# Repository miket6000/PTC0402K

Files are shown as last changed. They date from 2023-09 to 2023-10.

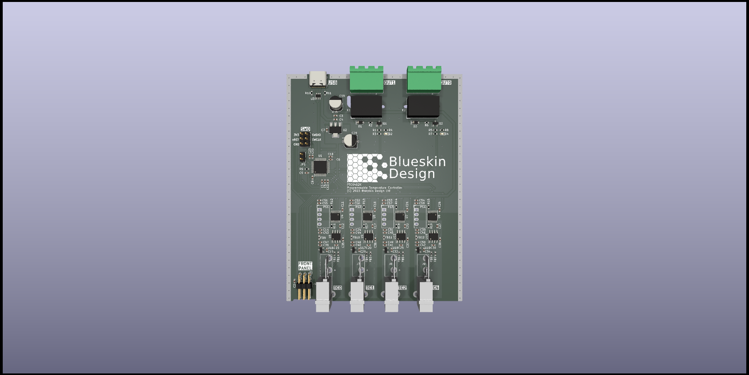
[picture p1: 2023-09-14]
documentation/3d_top_TemperatureLogger.png

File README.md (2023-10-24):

# PTC0402K
A fully isolated (channel to channel and channel to input) four channel, two output programmable temperature controller and logger.

3d_top_TemperatureLogger

This project was built with a few target features in mind:
- Four input channels with at least 0.5C accuracy.
- SCPI interface to interface cleanly with the rest of my lab setup.
- Complete isolation of each channel (at least 230VAC) both between channels and between mains. This allows you to put a thermocouple directly on a live heatsink without risk of damaging the device or anything attached to the other thermocouples.
- A couple of relay outputs for potentially controlling heaters or coolers to allow temperature control.
- USB Type-C for both power and communications for simple setup.

A lot of inspiration came from the very nice project by Jana Marie at https://github.com/Jana-Marie/temperature-logger 

## Status
### Hardware
Rev 1 hardware has arrived. There is a fault in the current schematic where the digital isolators all drive the DO lines, even when their CS line is high. This kills the entire SPI bus. In my Rev 1 hardware I have corrected this by adding a small N-Channel MOSFET between the isolator's output enable pin and ground which is switched by the CS line. This means that normally the output is disabled on all isolators, but is enabled when the CS line is pulled low.

A bigger issue appears to be the temperature error in measureing the cold side junction. Because of the proximity of the MAX31855 to the isolated DCDC converter (which gets warm) and the distance to the thermocouple connector, there can be an error in the reported cold side junction temperature. As thermocouples are differnetial temperature devices, this directly adds to the temperature of the measurement. It looks like this is somewhere in the vicinty of 2-3 degrees C, however this depends on the ambient temperature and how long the entire device is powered which makes it difficult to calibrate out. 

Rev 2 will include the CS line fix and also add external flash to allow on board logging. I'm debating the merits of including a 32kHz crystal for the built in RTC (but then, do I also want a backup battery...) and might end up upgrading the STM32F072 to an STM32F078 for the additional ROM. For the cold junction offset issue I'm still debating options. I could simply move the MAX31855 closer to the junction and further from the DCDC converter, or I could add an additional temperature sensor to the junction itself and provide proper automatic calibration in SW. If I go that path however I end up with a highly integrated solution where I'm effectively not relying on any of the integration and I'd probably be better off with a 16-24bit DAC and discrete voltage reference and an analogue muxer, however this would take up more board space and likely end up costing more.

### Software
A basic test firmware has been written which reads the hot and cold junction temperatures, as well as the thermocouple status and allows them to be read via SCPI. It also allows control of the output relays though no temperature controller or alarms have been written.

The math for computing the corrected NIST polynomial based temperatures is all calculated using fixed point math as there is no FPU in the STM32F072. Rather than computing the polynomials directly on the uC this was done offline to create a lookup table. This is both faster than using floats and more accurate than using fixed point the whole way through as we can use true double precision during intermediate steps of the calculations and only drop to the 16.16 fixed precision format for the final lookup.

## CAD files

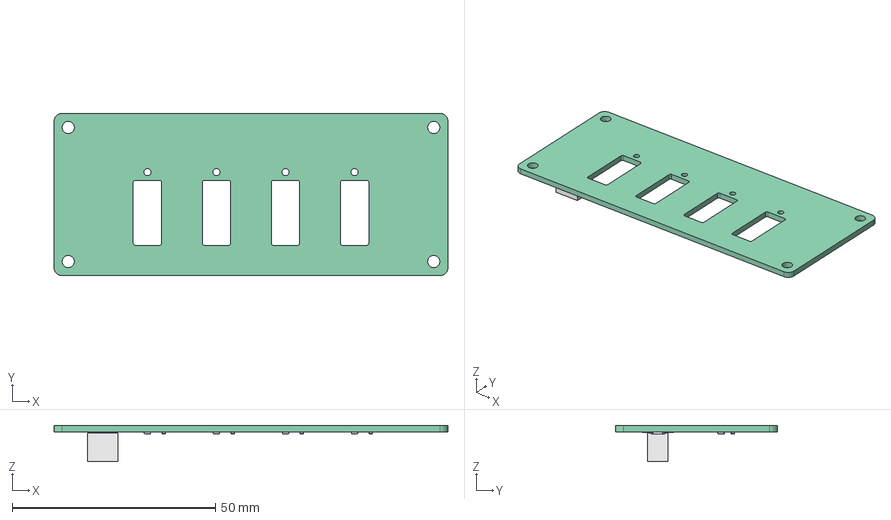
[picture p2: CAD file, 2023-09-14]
mechanical/Front.FCStd
97.0 x 40.0 x 8.90 mm
Pcb_1907
R5_R_0603_1608Metric_a8023c08d09b x 8
J1_PinSocket_2x03_P254mm_Vertical_SMD_16156b7471c3

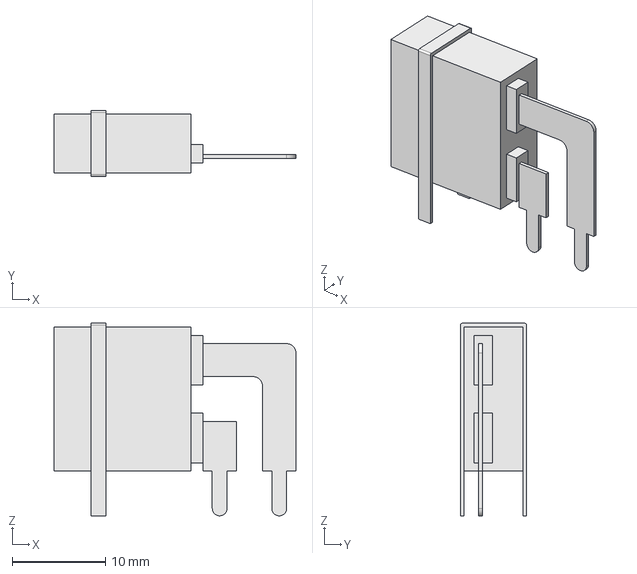
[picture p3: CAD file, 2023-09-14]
mechanical/PCC-SMP-V.FCStd
26.0 x 7.10 x 20.7 mm

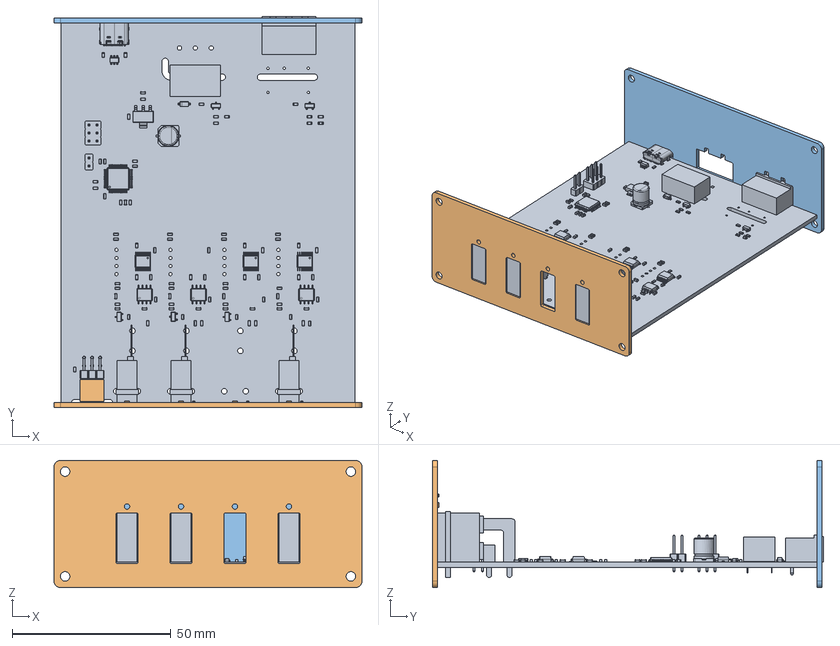
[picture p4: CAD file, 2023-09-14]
mechanical/Assemby.FCStd
97.0 x 123.3 x 40.0 mm
PCB_001
Front_001
Rear_001

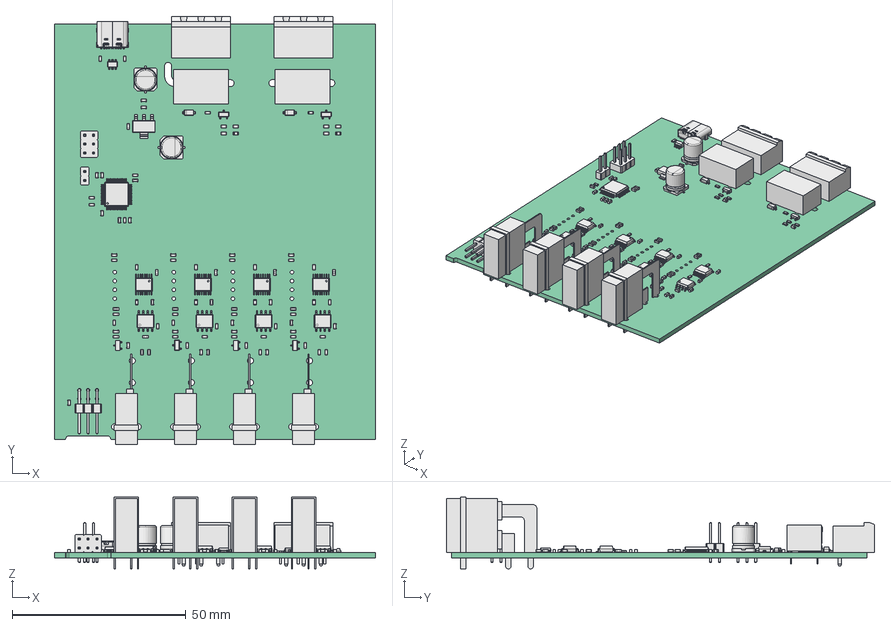
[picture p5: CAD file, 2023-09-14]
mechanical/PCB.FCStd
92.5 x 123.2 x 20.7 mm
Pcb_6b70
U19_SOT_23_b36488b32593 x 6
C33_C_0603_1608Metric_063d88e91227 x 57
J4_PinHeader_2x03_P254mm_Horizontal_694631943000
USB_C_Receptacle_16P_TopMnt_Horizontal_GCT_USB4105-xx-A
USB_C_Receptacle_16P_TopMnt_Horizontal_GCT_USB4105-xx-A001
USB_C_Receptacle_16P_TopMnt_Horizontal_GCT_USB4105-xx-A002
USB_C_Receptacle_16P_TopMnt_Horizontal_GCT_USB4105-xx-A003
USB_C_Receptacle_16P_TopMnt_Horizontal_GCT_USB4105-xx-A004
USB_C_Receptacle_16P_TopMnt_Horizontal_GCT_USB4105-xx-A005
USB_C_Receptacle_16P_TopMnt_Horizontal_GCT_USB4105-xx-A006
USB_C_Receptacle_16P_TopMnt_Horizontal_GCT_USB4105-xx-A007
USB_C_Receptacle_16P_TopMnt_Horizontal_GCT_USB4105-xx-A008
USB_C_Receptacle_16P_TopMnt_Horizontal_GCT_USB4105-xx-A009
USB_C_Receptacle_16P_TopMnt_Horizontal_GCT_USB4105-xx-A010
USB_C_Receptacle_16P_TopMnt_Horizontal_GCT_USB4105-xx-A011
USB_C_Receptacle_16P_TopMnt_Horizontal_GCT_USB4105-xx-A012
USB_C_Receptacle_16P_TopMnt_Horizontal_GCT_USB4105-xx-A013
USB_C_Receptacle_16P_TopMnt_Horizontal_GCT_USB4105-xx-A014
USB_C_Receptacle_16P_TopMnt_Horizontal_GCT_USB4105-xx-A015
USB_C_Receptacle_16P_TopMnt_Horizontal_GCT_USB4105-xx-A016
USB_C_Receptacle_16P_TopMnt_Horizontal_GCT_USB4105-xx-A017
USB_C_Receptacle_16P_TopMnt_Horizontal_GCT_USB4105-xx-A018
USB_C_Receptacle_16P_TopMnt_Horizontal_GCT_USB4105-xx-A019
USB_C_Receptacle_16P_TopMnt_Horizontal_GCT_USB4105-xx-A020
USB_C_Receptacle_16P_TopMnt_Horizontal_GCT_USB4105-xx-A021
USB_C_Receptacle_16P_TopMnt_Horizontal_GCT_USB4105-xx-A022
USB_C_Receptacle_16P_TopMnt_Horizontal_GCT_USB4105-xx-A023
USB_C_Receptacle_16P_TopMnt_Horizontal_GCT_USB4105-xx-A024
USB_C_Receptacle_16P_TopMnt_Horizontal_GCT_USB4105-xx-A025
USB_C_Receptacle_16P_TopMnt_Horizontal_GCT_USB4105-xx-A026
USB_C_Receptacle_16P_TopMnt_Horizontal_GCT_USB4105-xx-A027
USB_C_Receptacle_16P_TopMnt_Horizontal_GCT_USB4105-xx-A028
USB_C_Receptacle_16P_TopMnt_Horizontal_GCT_USB4105-xx-A029
USB_C_Receptacle_16P_TopMnt_Horizontal_GCT_USB4105-xx-A030
USB_C_Receptacle_16P_TopMnt_Horizontal_GCT_USB4105-xx-A031
USB_C_Receptacle_16P_TopMnt_Horizontal_GCT_USB4105-xx-A032
USB_C_Receptacle_16P_TopMnt_Horizontal_GCT_USB4105-xx-A033
USB_C_Receptacle_16P_TopMnt_Horizontal_GCT_USB4105-xx-A034
USB_C_Receptacle_16P_TopMnt_Horizontal_GCT_USB4105-xx-A035
FB2_L_0603_1608Metric_c892ebd92c1a x 12
K2_Relay_SPDT_Omron_G6E_e7cbb446817c x 2
R13_R_0603_1608Metric_337461c32d41 x 19
J8_Body_0be8fa092d88 x 4
J5_PinHeader_2x03_P254mm_Vertical_61c661ac012c
U5_SSOP_16_39x49mm_P0635mm_b9b537abdd21 x 4
U1_LQFP_48_7x7mm_P05mm_b04207c67cd0
D3_D_SOD_123_1aa070bb9a73 x 2
U12_SOIC_8_39x49mm_P127mm_51daad1ce575 x 4
D2_LED_0603_1608Metric_81a1771d8797 x 2
C59_CP_Elec_63x77_526fc9ffda22 x 2
U3_SOT_23_6_5fe2d78700b6
U2_SOT_223_7fa0f1d7f736
J1_MSTBA_01x03_G_5_00mm_6adaa229897f x 2
JP1_PinHeader_1x02_P254mm_Vertical_b7242ec4fe1f

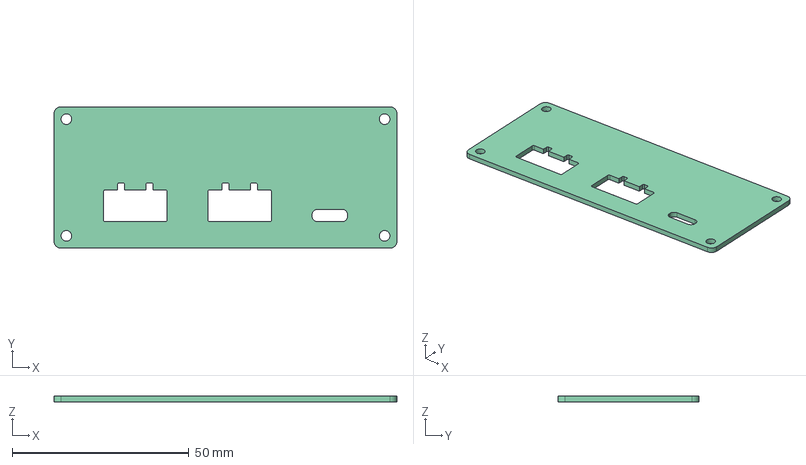
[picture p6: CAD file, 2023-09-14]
mechanical/Rear.FCStd
97.0 x 40.0 x 1.60 mm

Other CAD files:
mechanical/PCC-SMP-V-Body.step

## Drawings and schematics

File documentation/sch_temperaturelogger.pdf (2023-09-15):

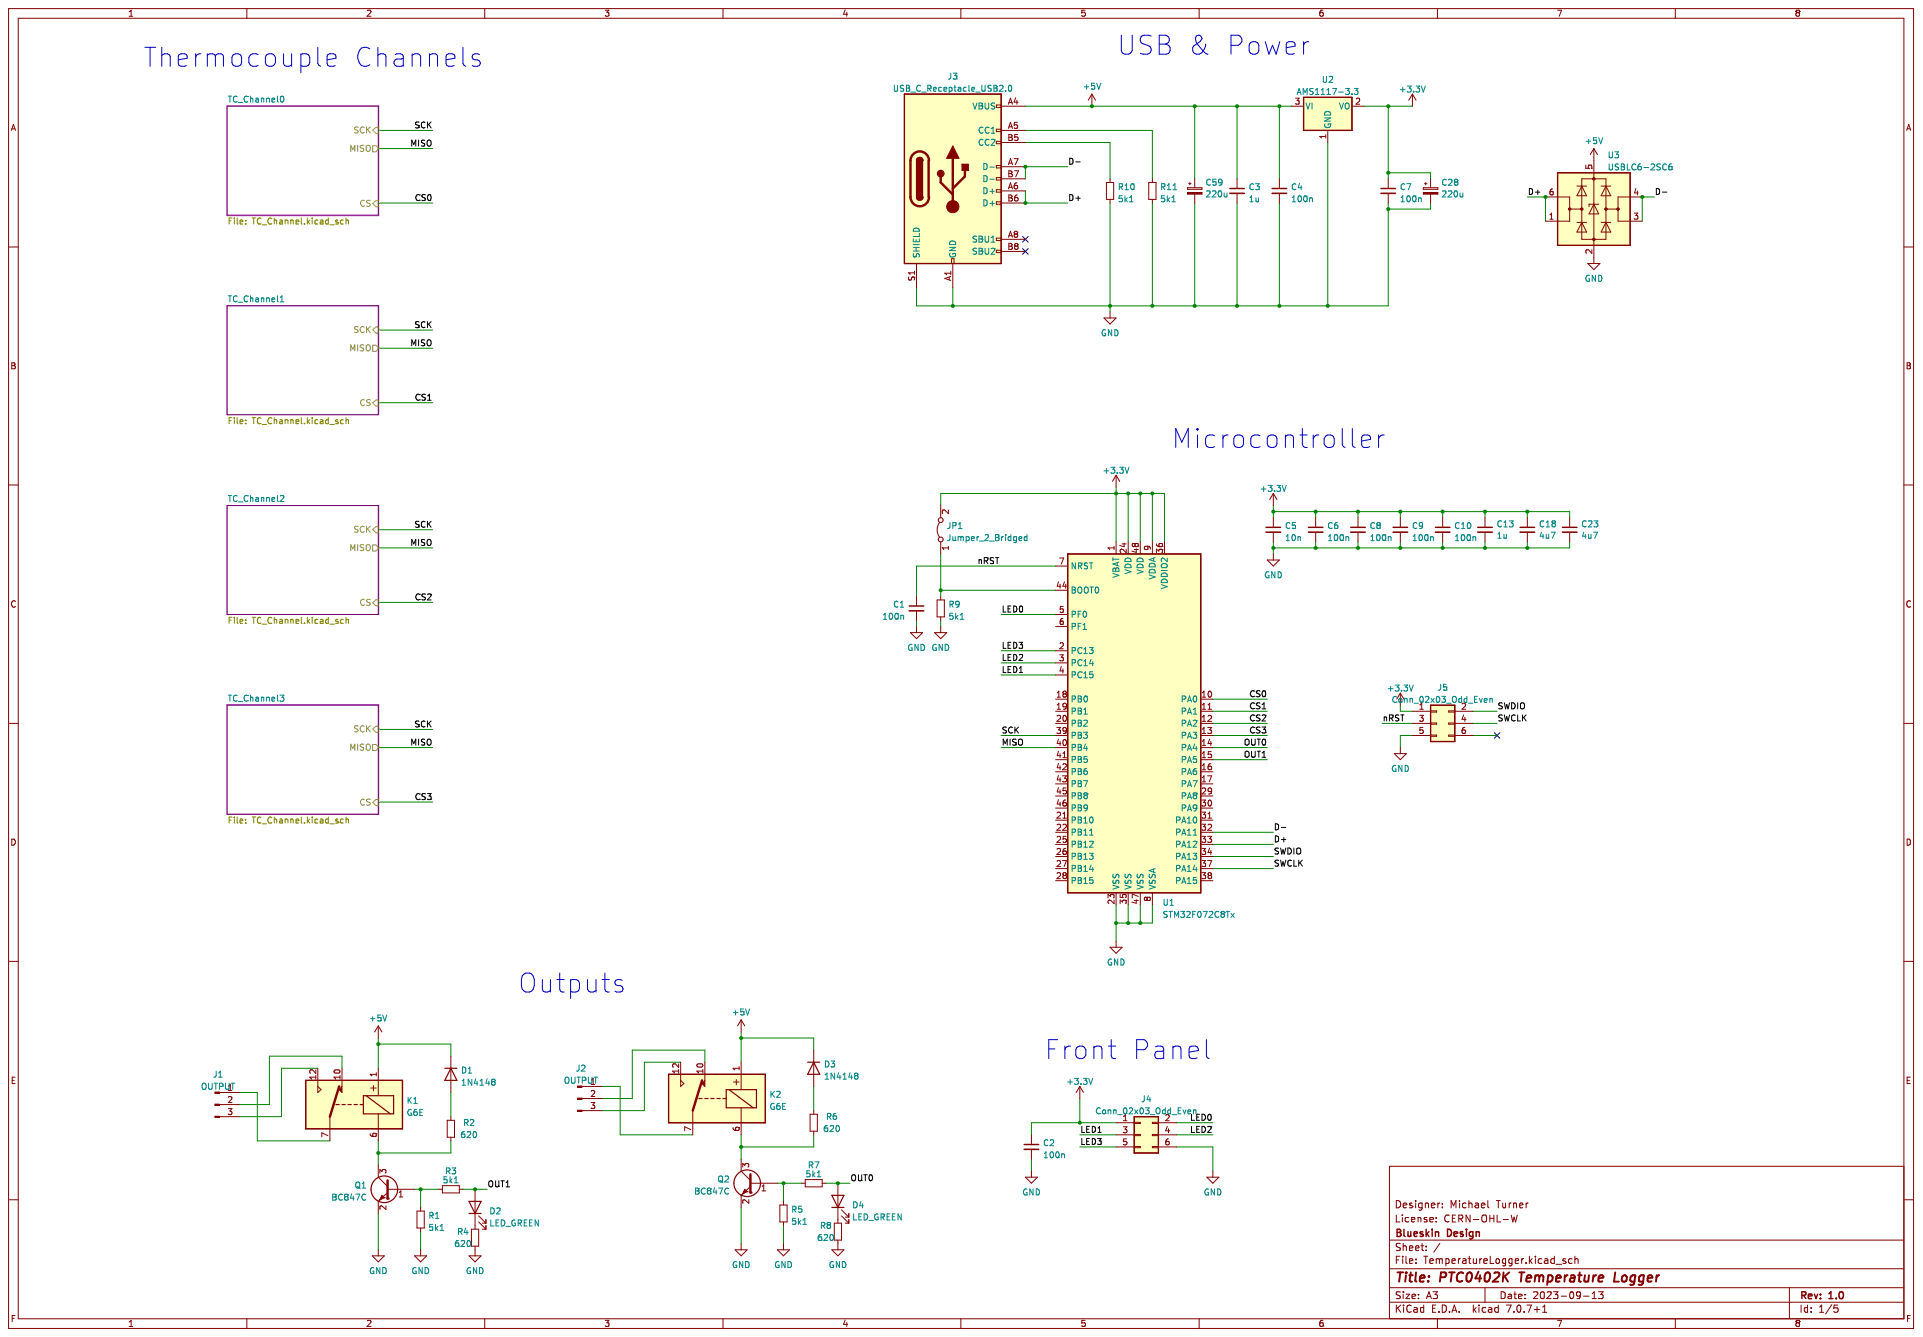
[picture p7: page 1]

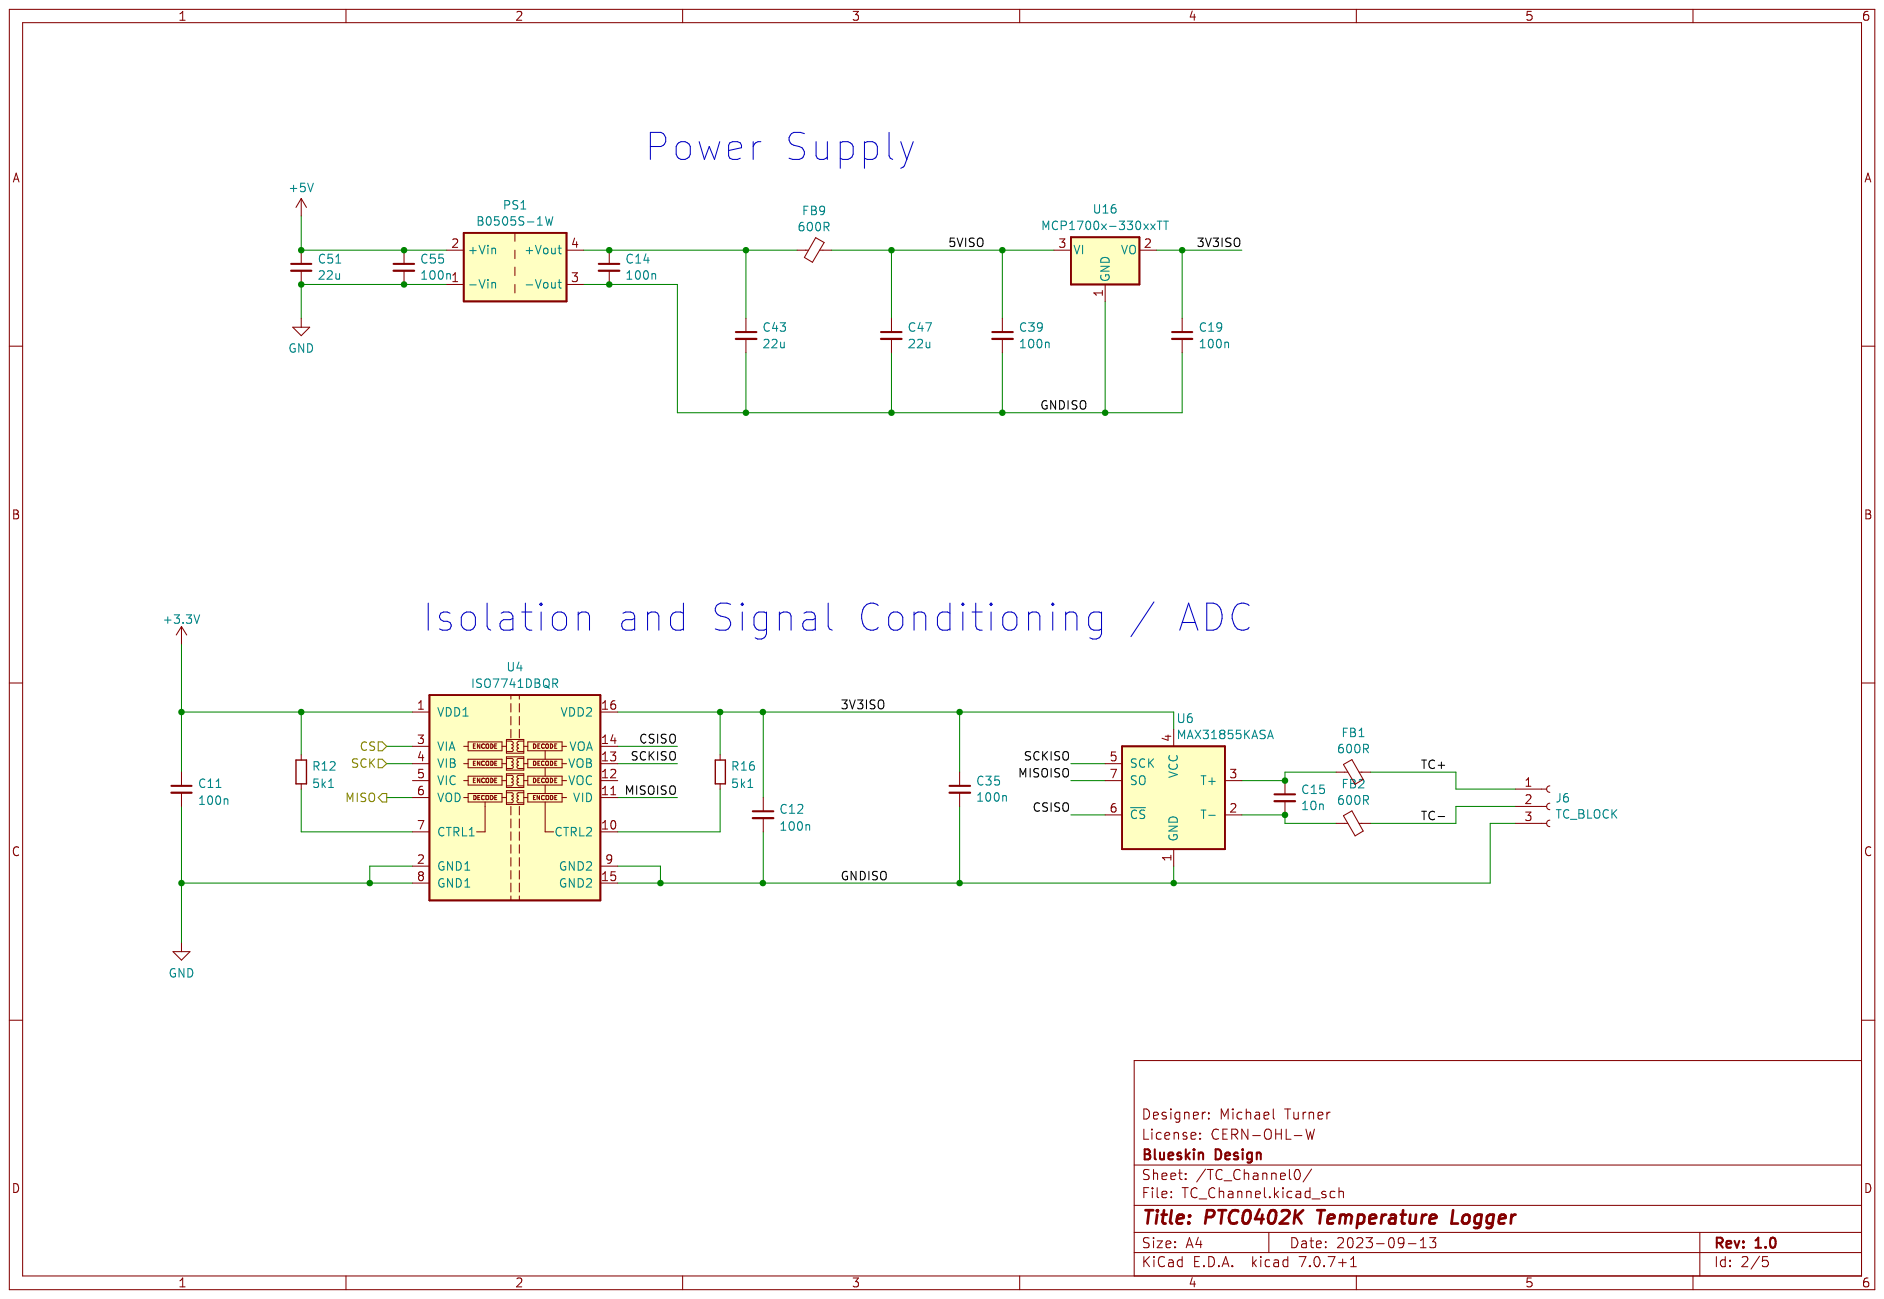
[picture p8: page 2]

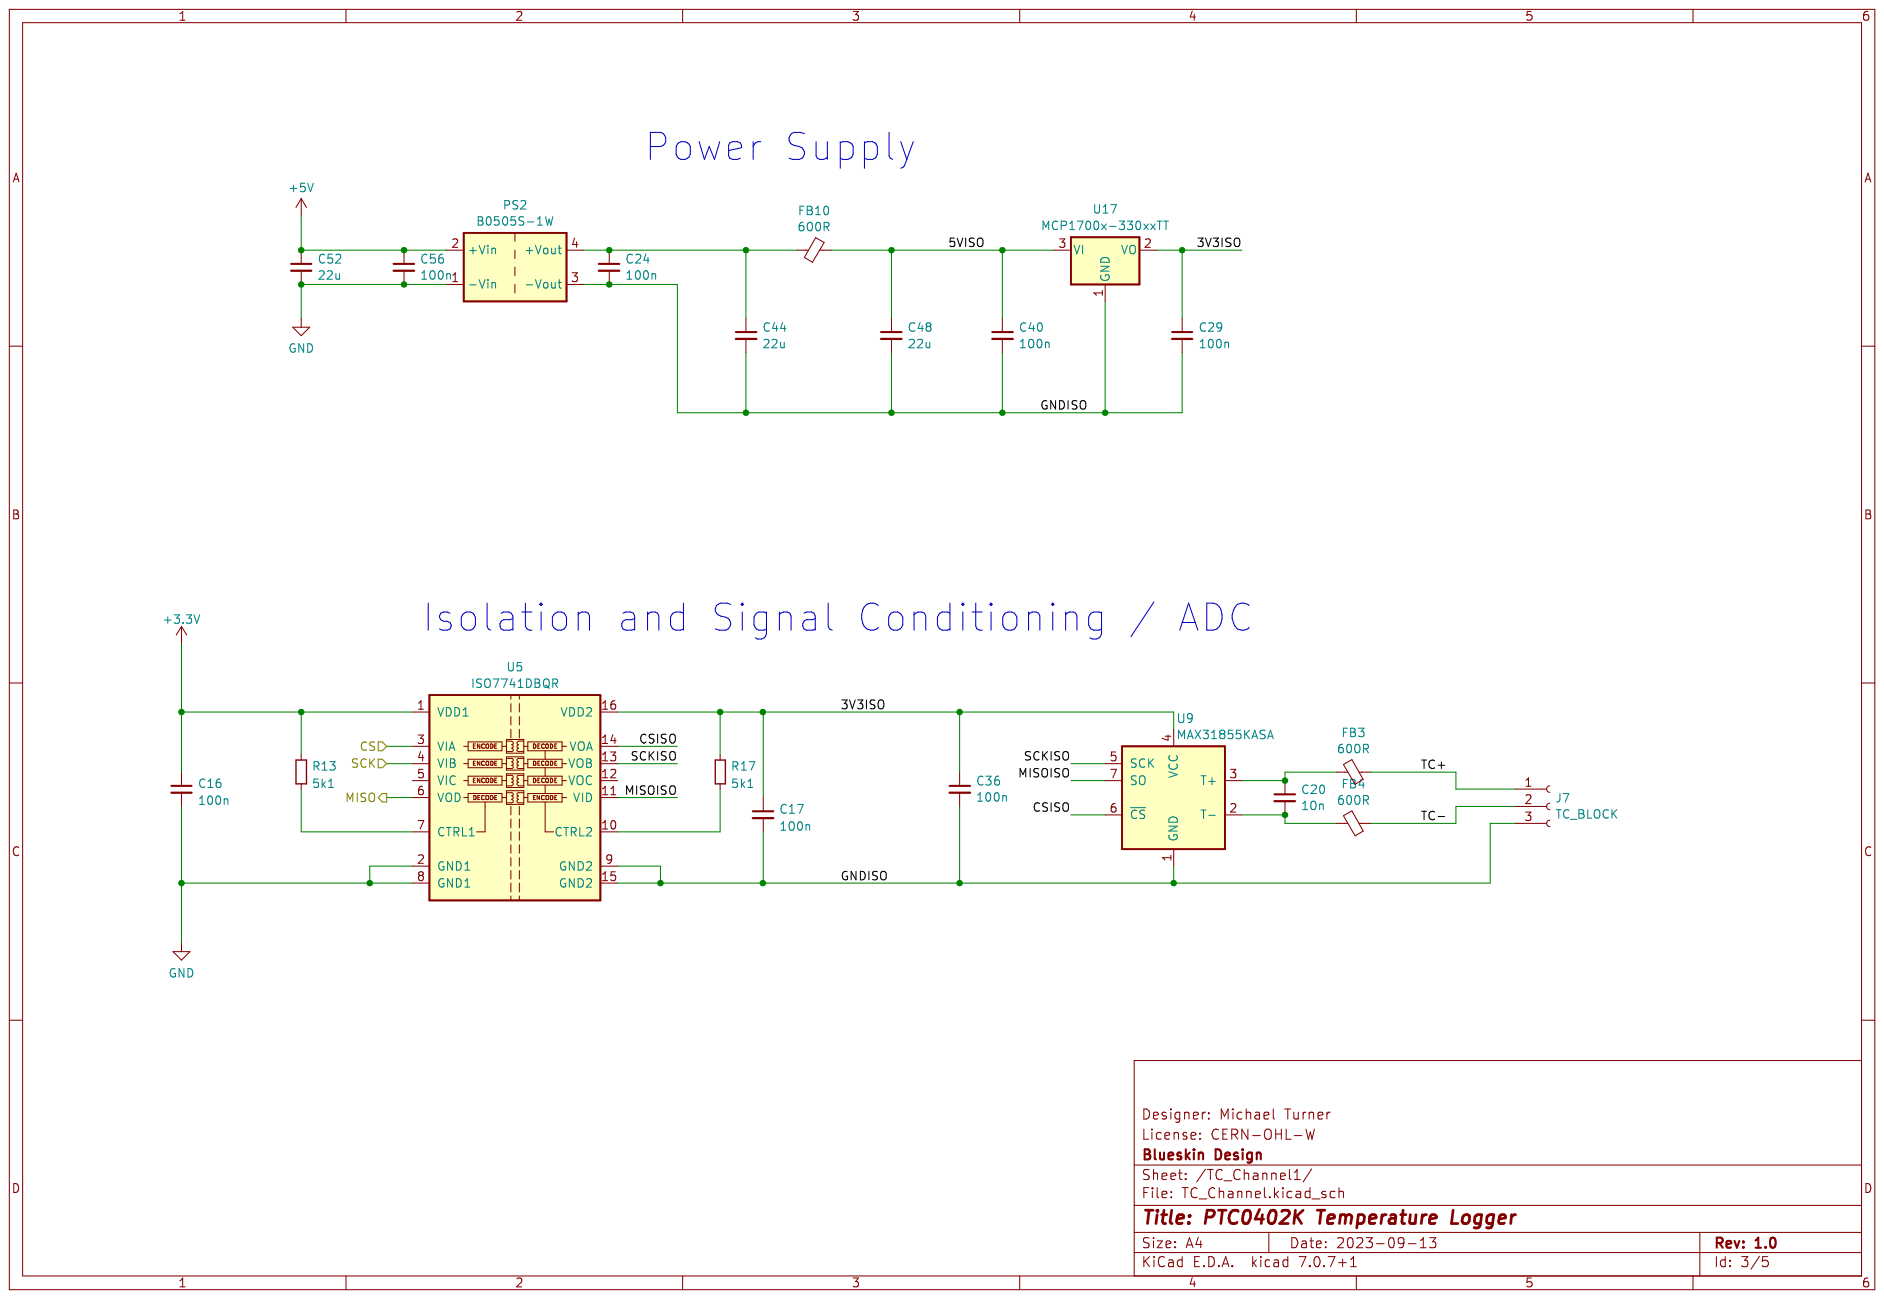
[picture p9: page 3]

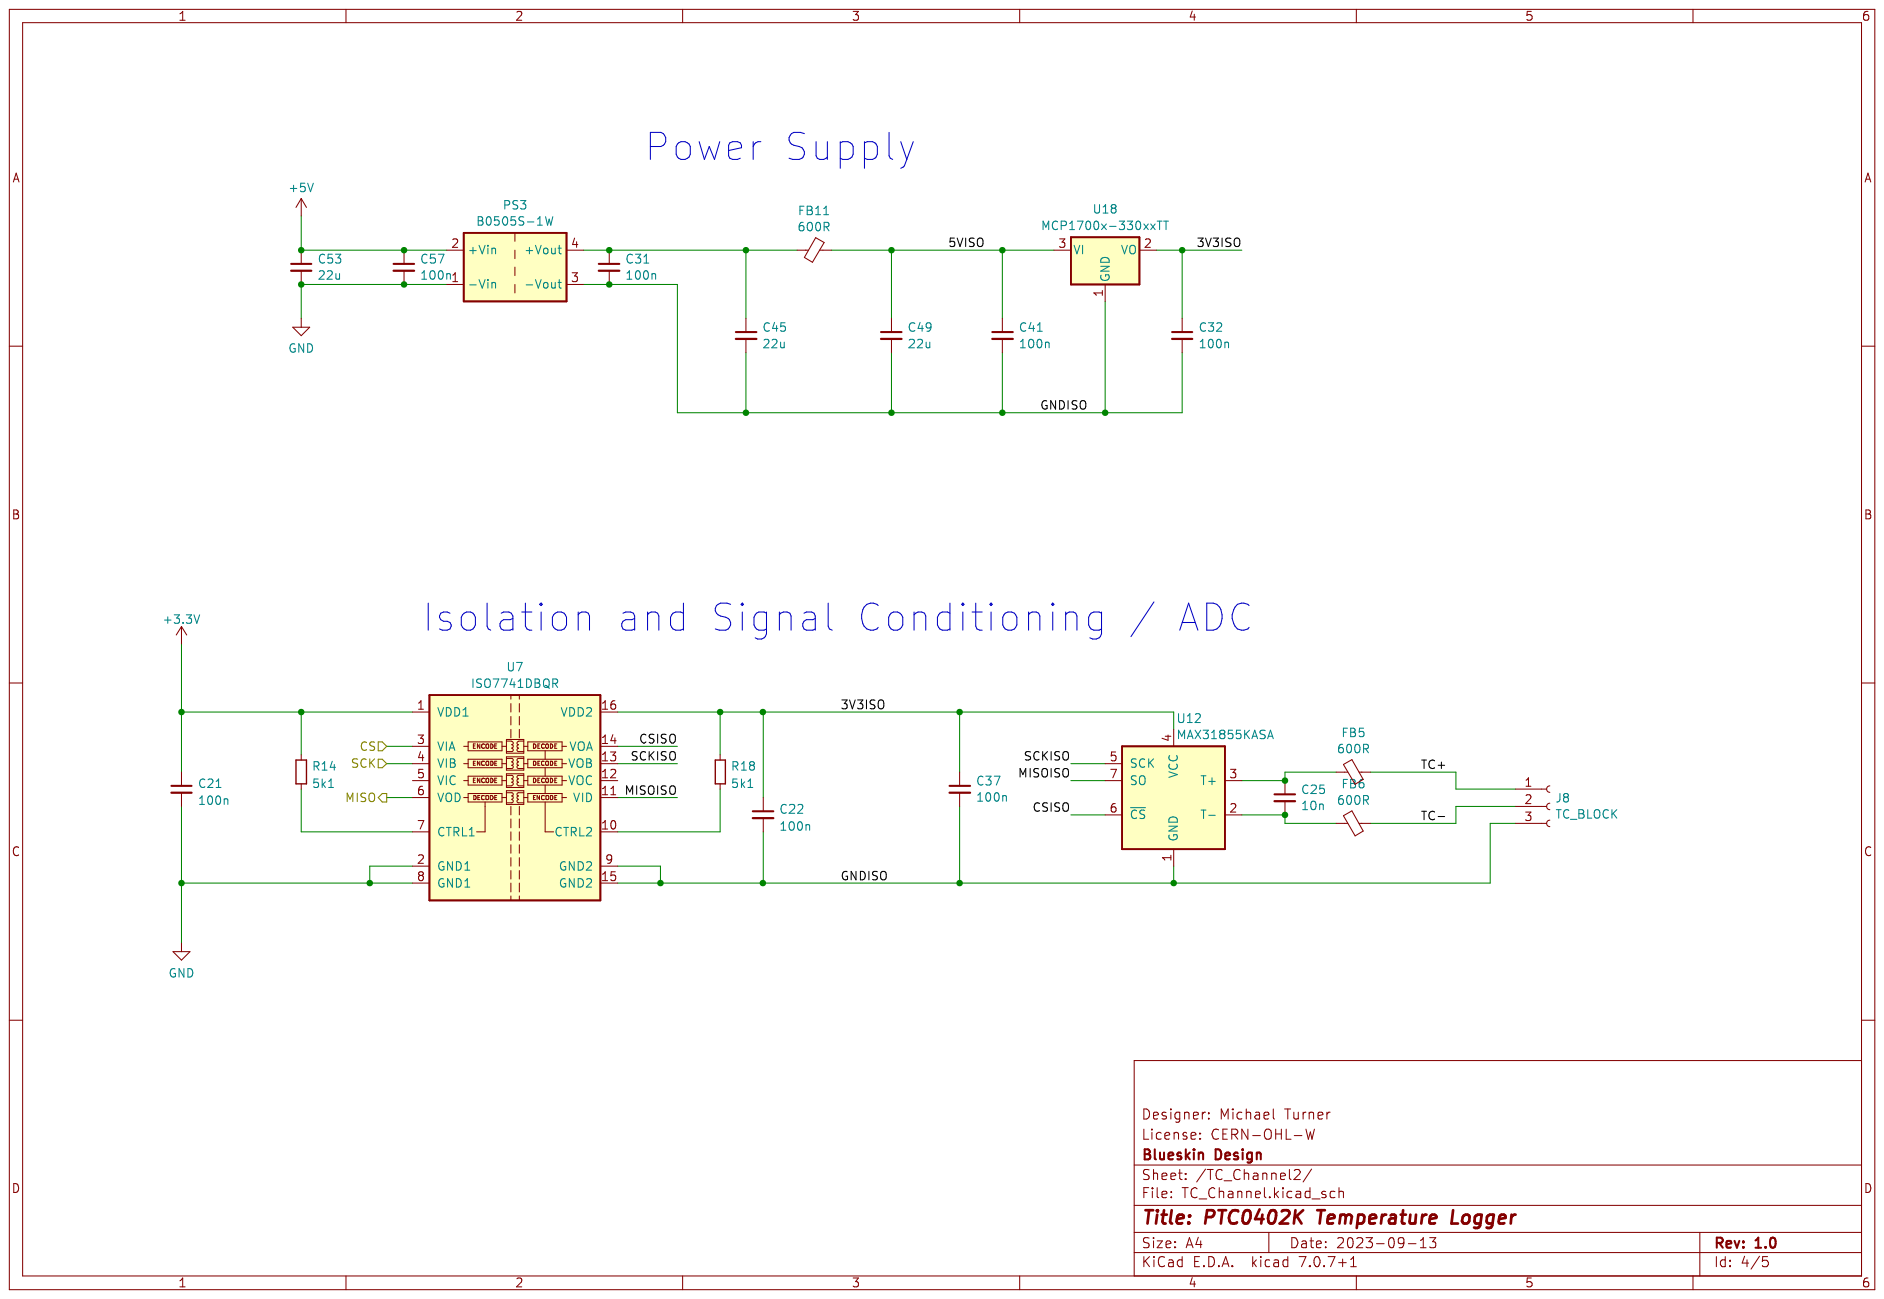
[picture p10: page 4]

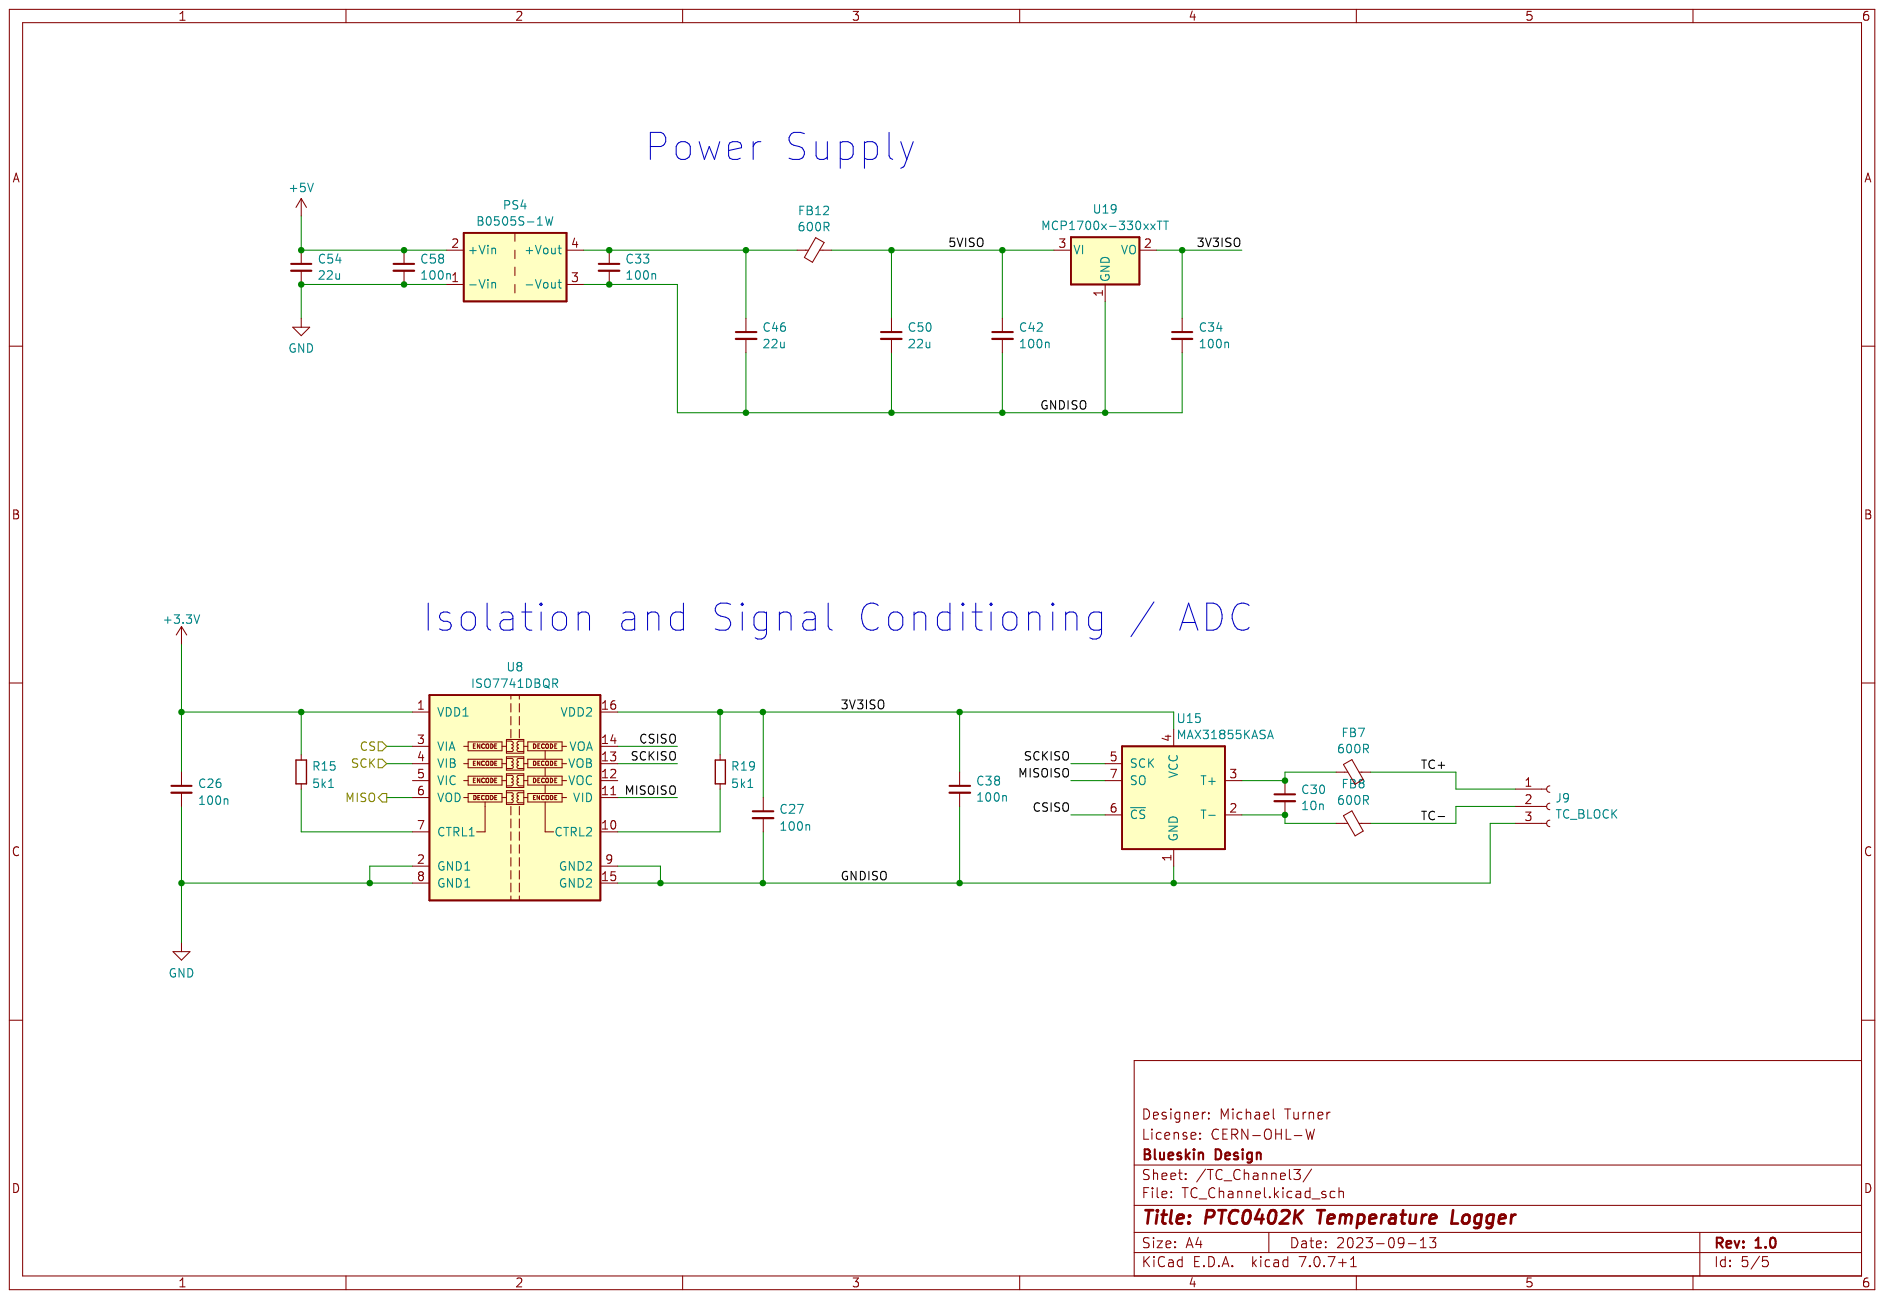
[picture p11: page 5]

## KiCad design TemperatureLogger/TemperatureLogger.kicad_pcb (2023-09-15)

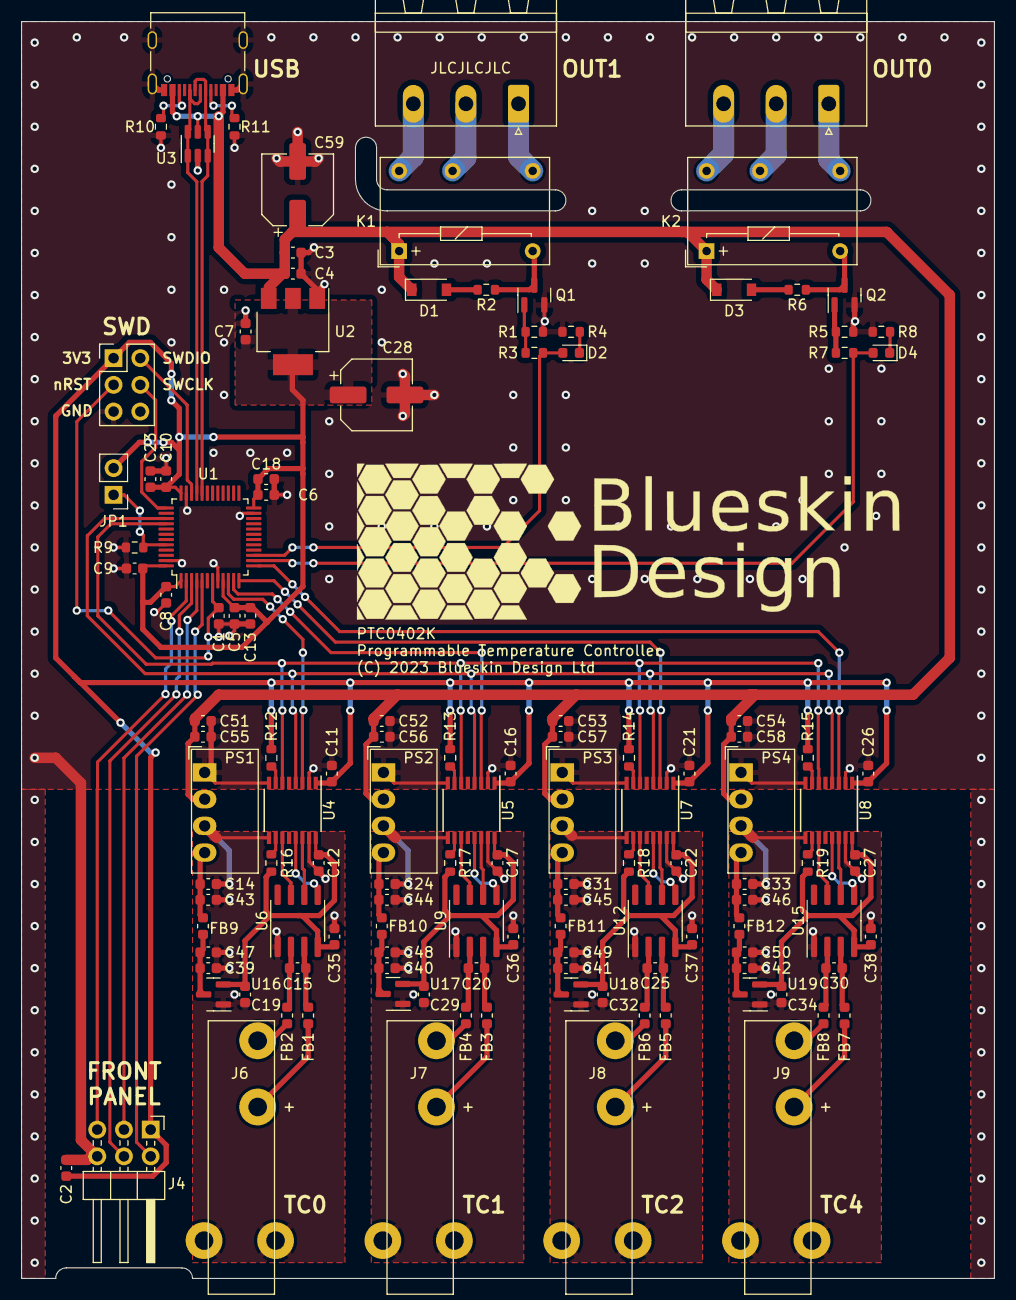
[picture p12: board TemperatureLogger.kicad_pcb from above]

Board: 2 copper layers, 92.5 x 119.5 mm, 127 parts (0 on the bottom side), 89 nets.

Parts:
C1, C2, C4, C6, C7, C8, C9, C10, C11, C12, C14, C16, C17, C19, C21, C22, C24, C26, C27, C29, C31, C32, C33, C34, C35, C36, C37, C38, C39, C40, C41, C42, C55, C56, C57, C58: 100n; C_0603_1608Metric
C3, C13: 1u; C_0603_1608Metric
C5, C15, C20, C25, C30: 10n; C_0603_1608Metric
C18, C23: 4u7; C_0603_1608Metric
C28, C59: 220u; CP_Elec_6.3x7.7
C43, C44, C45, C46, C47, C48, C49, C50, C51, C52, C53, C54: 22u; C_0603_1608Metric
D1, D3: 1N4148; D_SOD-123
D2, D4: LED_GREEN; LED_0603_1608Metric
FB1, FB2, FB3, FB4, FB5, FB6, FB7, FB8, FB9, FB10, FB11, FB12: 600R; L_0603_1608Metric
J1, J2: OUTPUT; PhoenixContact_MSTBA_2,5_3-G_1x03_P5.00mm_Horizontal
J3: USB_C_Receptacle_USB2.0; USB_C_Receptacle_Palconn_UTC16-G
J4: Conn_02x03_Odd_Even; PinHeader_2x03_P2.54mm_Horizontal
J5: Conn_02x03_Odd_Even; PinHeader_2x03_P2.54mm_Vertical
J6, J7, J8, J9: TC_BLOCK; PCC-SMP-V
JP1: Jumper_2_Bridged; PinHeader_1x02_P2.54mm_Vertical
K1, K2: G6E; Relay_SPDT_Omron_G6E
PS1, PS2, PS3, PS4: B0505S-1W; Converter_DCDC_Murata_MEE1SxxxxSC_THT
Q1, Q2: BC847C; SOT-23
R1, R3, R5, R7, R9, R10, R11, R12, R13, R14, R15, R16, R17, R18, R19: 5k1; R_0603_1608Metric
R2, R4, R6, R8: 620; R_0603_1608Metric
U1: STM32F072C8Tx; LQFP-48_7x7mm_P0.5mm
U2: AMS1117-3.3; SOT-223-3_TabPin2
U3: USBLC6-2SC6; SOT-23-6
U4, U5, U7, U8: ISO7741DBQR; SSOP-16_3.9x4.9mm_P0.635mm
U6, U9, U12, U15: MAX31855KASA; SOIC-8_3.9x4.9mm_P1.27mm
U16, U17, U18, U19: MCP1700x-330xxTT; SOT-23

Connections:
+3.3V: C2.1, C5.1, C6.1, C7.1, C8.1, C9.1, C10.1, C11.1, C13.1, C16.1, C18.1, C21.1, C23.1, C26.1, C28.1, J4.1, J5.1, JP1.2 (B), R12.2, R13.2, R14.2, R15.2, U1.1 (VBAT), U1.9 (VDDA), U1.24 (VDD), U1.36 (VDDIO2), U1.48 (VDD), U2.2 (VO), U4.1 (VDD1), U5.1 (VDD1), U7.1 (VDD1), U8.1 (VDD1)
+5V: C3.1, C4.1, C51.1, C52.1, C53.1, C54.1, C55.1, C56.1, C57.1, C58.1, C59.1, D1.1 (K), D3.1 (K), J3.A4 (VBUS), J3.A9 (VBUS), J3.B4 (VBUS), J3.B9 (VBUS), K1.1, K2.1, PS1.2 (+Vin), PS2.2 (+Vin), PS3.2 (+Vin), PS4.2 (+Vin), U2.3 (VI), U3.5 (VBUS)
/CS0: U1.10 (PA0), U4.3 (VIA)
/CS1: U1.11 (PA1), U5.3 (VIA)
/CS2: U1.12 (PA2), U7.3 (VIA)
/CS3: U1.13 (PA3), U8.3 (VIA)
/D+: J3.A6 (D+), J3.B6 (D+), U1.33 (PA12), U3.1 (I/O1), U3.6 (I/O1)
/D-: J3.A7 (D-), J3.B7 (D-), U1.32 (PA11), U3.3 (I/O2), U3.4 (I/O2)
/LED0: J4.2, U1.5 (PF0)
/LED1: J4.3, U1.4 (PC15)
/LED2: J4.4, U1.3 (PC14)
/LED3: J4.5, U1.2 (PC13)
/MISO: U1.40 (PB4), U4.6 (VOD), U5.6 (VOD), U7.6 (VOD), U8.6 (VOD)
/OUT0: D4.2 (A), R7.2, U1.14 (PA4)
/OUT1: D2.2 (A), R3.2, U1.15 (PA5)
/SCK: U1.39 (PB3), U4.4 (VIB), U5.4 (VIB), U7.4 (VIB), U8.4 (VIB)
/SWCLK: J5.4, U1.37 (PA14)
/SWDIO: J5.2, U1.34 (PA13)
/TC_Channel0/3V3ISO: C12.1, C19.1, C35.1, R16.2, U4.16 (VDD2), U6.4 (VCC), U16.2 (VO)
/TC_Channel0/5VISO: C39.1, C47.1, FB9.2, U16.3 (VI)
/TC_Channel0/CSISO: U4.14 (VOA), U6.6 (~CS)
/TC_Channel0/GNDISO: C12.2, C14.2, C19.2, C35.2, C39.2, C43.2, C47.2, J6.3, PS1.3 (-Vout), U4.9 (GND2), U4.15 (GND2), U6.1 (GND), U16.1 (GND)
/TC_Channel0/MISOISO: U4.11 (VID), U6.7 (SO)
/TC_Channel0/SCKISO: U4.13 (VOB), U6.5 (SCK)
/TC_Channel0/TC+: FB1.1, J6.1
/TC_Channel0/TC-: FB2.1, J6.2
/TC_Channel1/3V3ISO: C17.1, C29.1, C36.1, R17.2, U5.16 (VDD2), U9.4 (VCC), U17.2 (VO)
/TC_Channel1/5VISO: C40.1, C48.1, FB10.2, U17.3 (VI)
/TC_Channel1/CSISO: U5.14 (VOA), U9.6 (~CS)
/TC_Channel1/GNDISO: C17.2, C24.2, C29.2, C36.2, C40.2, C44.2, C48.2, J7.3, PS2.3 (-Vout), U5.9 (GND2), U5.15 (GND2), U9.1 (GND), U17.1 (GND)
/TC_Channel1/MISOISO: U5.11 (VID), U9.7 (SO)
/TC_Channel1/SCKISO: U5.13 (VOB), U9.5 (SCK)
/TC_Channel1/TC+: FB3.1, J7.1
/TC_Channel1/TC-: FB4.1, J7.2
/TC_Channel2/3V3ISO: C22.1, C32.1, C37.1, R18.2, U7.16 (VDD2), U12.4 (VCC), U18.2 (VO)
/TC_Channel2/5VISO: C41.1, C49.1, FB11.2, U18.3 (VI)
/TC_Channel2/CSISO: U7.14 (VOA), U12.6 (~CS)
/TC_Channel2/GNDISO: C22.2, C31.2, C32.2, C37.2, C41.2, C45.2, C49.2, J8.3, PS3.3 (-Vout), U7.9 (GND2), U7.15 (GND2), U12.1 (GND), U18.1 (GND)
/TC_Channel2/MISOISO: U7.11 (VID), U12.7 (SO)
/TC_Channel2/SCKISO: U7.13 (VOB), U12.5 (SCK)
/TC_Channel2/TC+: FB5.1, J8.1
/TC_Channel2/TC-: FB6.1, J8.2
/TC_Channel3/3V3ISO: C27.1, C34.1, C38.1, R19.2, U8.16 (VDD2), U15.4 (VCC), U19.2 (VO)
/TC_Channel3/5VISO: C42.1, C50.1, FB12.2, U19.3 (VI)
/TC_Channel3/CSISO: U8.14 (VOA), U15.6 (~CS)
/TC_Channel3/GNDISO: C27.2, C33.2, C34.2, C38.2, C42.2, C46.2, C50.2, J9.3, PS4.3 (-Vout), U8.9 (GND2), U8.15 (GND2), U15.1 (GND), U19.1 (GND)
/TC_Channel3/MISOISO: U8.11 (VID), U15.7 (SO)
/TC_Channel3/SCKISO: U8.13 (VOB), U15.5 (SCK)
/TC_Channel3/TC+: FB7.1, J9.1
/TC_Channel3/TC-: FB8.1, J9.2
/nRST: C1.1, J5.3, U1.7 (NRST)
GND: C1.2, C2.2, C3.2, C4.2, C5.2, C6.2, C7.2, C8.2, C9.2, C10.2, C11.2, C13.2, C16.2, C18.2, C21.2, C23.2, C26.2, C28.2, C51.2, C52.2, C53.2, C54.2, C55.2, C56.2, C57.2, C58.2, C59.2, J3.A1 (GND), J3.A12 (GND), J3.B1 (GND), J3.B12 (GND), J3.S1 (SHIELD), J4.6, J5.5, PS1.1 (-Vin), PS2.1 (-Vin), PS3.1 (-Vin), PS4.1 (-Vin), Q1.2 (E), Q2.2 (E), R1.1, R4.1, R5.1, R8.1, R9.2, R10.2, R11.2, U1.8 (VSSA), U1.23 (VSS), U1.35 (VSS), U1.47 (VSS), U2.1 (GND), U3.2 (GND), U4.2 (GND1), U4.8 (GND1), U5.2 (GND1), U5.8 (GND1), U7.2 (GND1), U7.8 (GND1), U8.2 (GND1), U8.8 (GND1)
unnamed: D1.2 (A), R2.2
unnamed: D2.1 (K), R4.2
unnamed: D3.2 (A), R6.2
unnamed: D4.1 (K), R8.2
unnamed: J1.1, K1.7
unnamed: J1.2, K1.10
unnamed: J1.3, K1.12
unnamed: J2.1, K2.7
unnamed: J2.2, K2.10
unnamed: J2.3, K2.12
unnamed: J3.A5 (CC1), R11.1
unnamed: J3.B5 (CC2), R10.1
unnamed: JP1.1 (A), R9.1, U1.44 (BOOT0)
unnamed: C14.1, C43.1, FB9.1, PS1.4 (+Vout)
unnamed: C24.1, C44.1, FB10.1, PS2.4 (+Vout)
unnamed: C31.1, C45.1, FB11.1, PS3.4 (+Vout)
unnamed: C33.1, C46.1, FB12.1, PS4.4 (+Vout)
unnamed: Q1.1 (B), R1.2, R3.1
unnamed: K1.6, Q1.3 (C), R2.1
unnamed: Q2.1 (B), R5.2, R7.1
unnamed: K2.6, Q2.3 (C), R6.1
unnamed: R12.1, U4.7 (CTRL1)
unnamed: R16.1, U4.10 (CTRL2)
unnamed: R13.1, U5.7 (CTRL1)
unnamed: R17.1, U5.10 (CTRL2)
unnamed: C15.1, FB1.2, U6.3 (T+)
unnamed: C15.2, FB2.2, U6.2 (T-)
unnamed: R14.1, U7.7 (CTRL1)
unnamed: R18.1, U7.10 (CTRL2)
unnamed: R15.1, U8.7 (CTRL1)
unnamed: R19.1, U8.10 (CTRL2)
unnamed: C20.1, FB3.2, U9.3 (T+)
unnamed: C20.2, FB4.2, U9.2 (T-)
unnamed: C25.1, FB5.2, U12.3 (T+)
unnamed: C25.2, FB6.2, U12.2 (T-)
unnamed: C30.1, FB7.2, U15.3 (T+)
unnamed: C30.2, FB8.2, U15.2 (T-)

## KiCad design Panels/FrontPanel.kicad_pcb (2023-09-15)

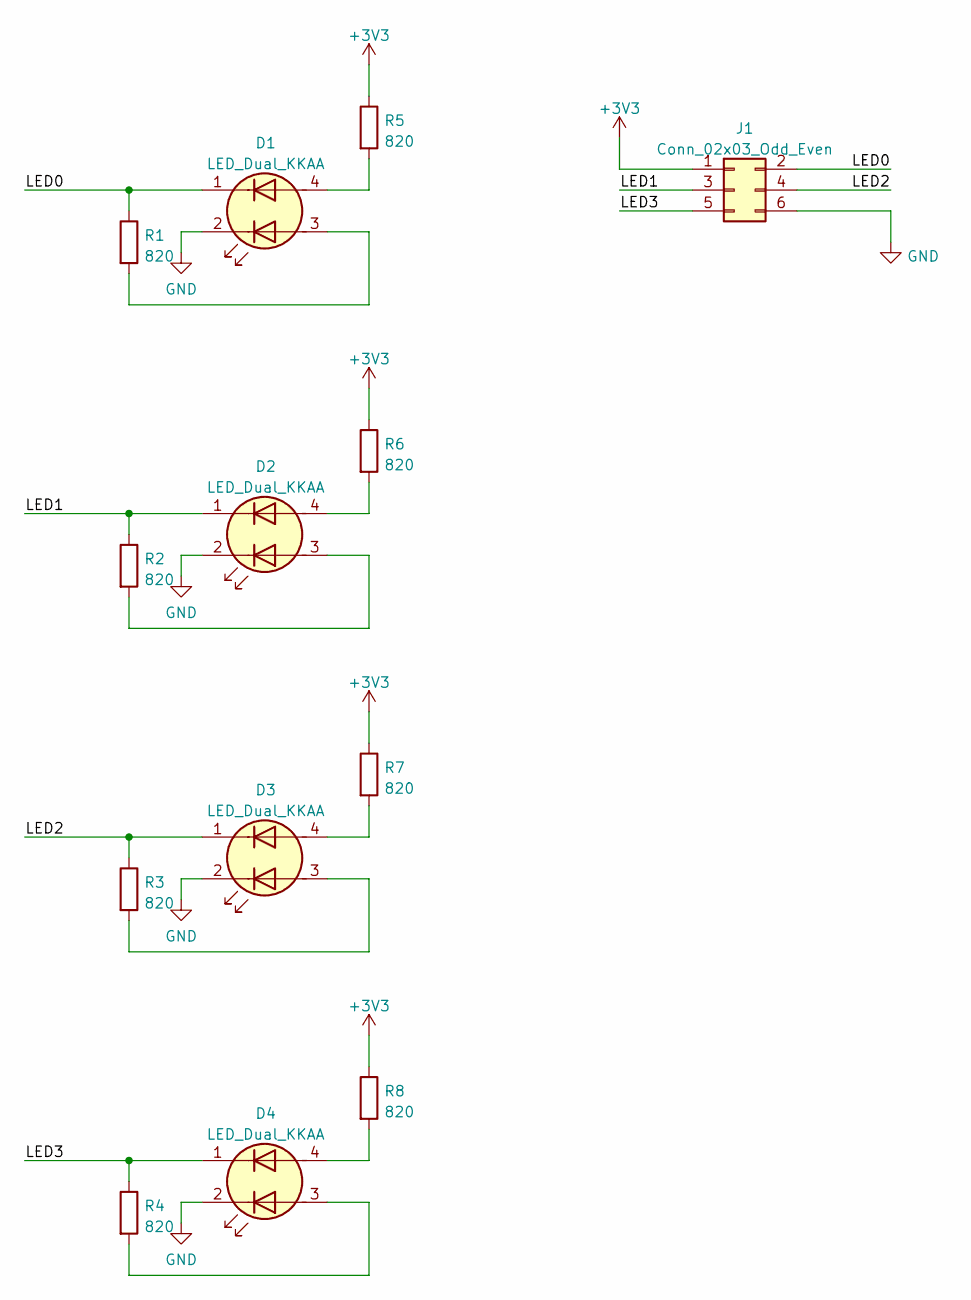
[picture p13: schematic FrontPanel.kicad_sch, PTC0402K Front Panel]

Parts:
D1, D2, D3, D4: LED_Dual_KKAA; Wurth_Bicolor_Reverse_Mount_LED
J1: Conn_02x03_Odd_Even; PinSocket_2x03_P2.54mm_Vertical_SMD
R1, R2, R3, R4, R5, R6, R7, R8: 820; R_0603_1608Metric_Pad0.98x0.95mm_HandSolder

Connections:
+3V3: J1.1, R5.1, R6.1, R7.1, R8.1
/LED0: D1.1 (K2), J1.2, R1.1
/LED1: D2.1 (K2), J1.3, R2.1
/LED2: D3.1 (K2), J1.4, R3.1
/LED3: D4.1 (K2), J1.5, R4.1
GND: D1.2 (K1), D2.2 (K1), D3.2 (K1), D4.2 (K1), J1.6
unnamed: D1.3 (A1), R1.2
unnamed: D1.4 (A2), R5.2
unnamed: D2.3 (A1), R2.2
unnamed: D2.4 (A2), R6.2
unnamed: D3.3 (A1), R3.2
unnamed: D3.4 (A2), R7.2
unnamed: D4.3 (A1), R4.2
unnamed: D4.4 (A2), R8.2

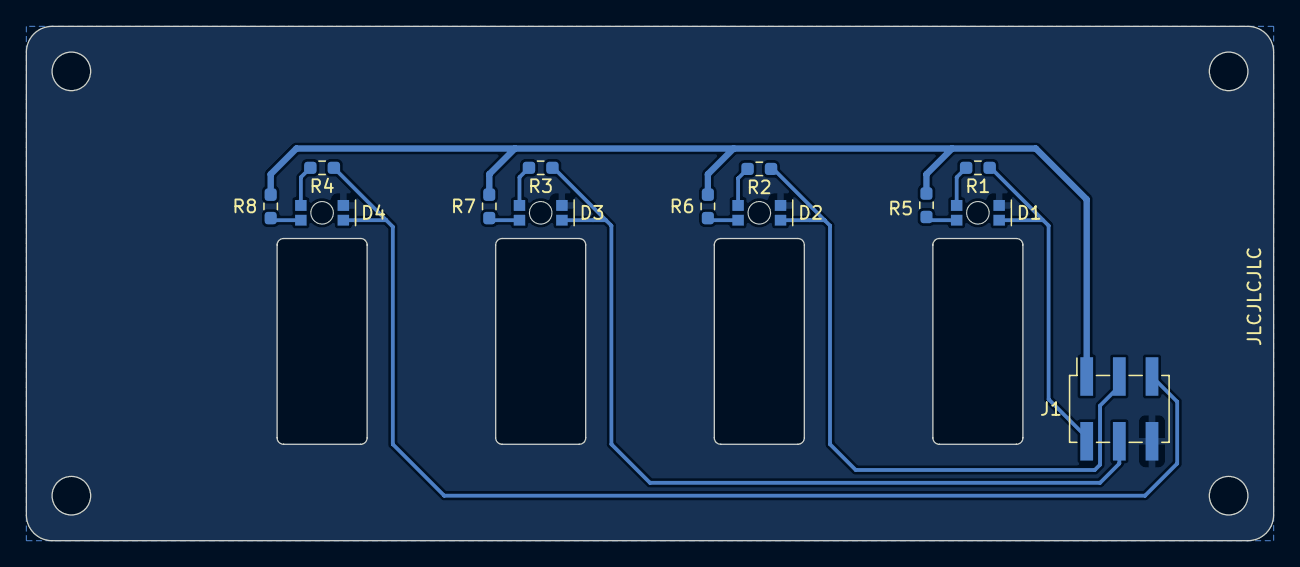
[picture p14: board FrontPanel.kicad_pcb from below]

Board: 2 copper layers, 97.0 x 40.0 mm, 13 parts (13 on the bottom side), 14 nets.

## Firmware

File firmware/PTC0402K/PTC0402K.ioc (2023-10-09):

#MicroXplorer Configuration settings - do not modify
CAD.formats=[{"id"\:42,"cad_product"\:"KiCAD v6+","cad_family"\:"KiCAD"}]
CAD.pinconfig=Dual
CAD.provider=
Dma.Request0=SPI1_RX
Dma.RequestsNb=1
Dma.SPI1_RX.0.Direction=DMA_PERIPH_TO_MEMORY
Dma.SPI1_RX.0.Instance=DMA1_Channel2
Dma.SPI1_RX.0.MemDataAlignment=DMA_MDATAALIGN_BYTE
Dma.SPI1_RX.0.MemInc=DMA_MINC_ENABLE
Dma.SPI1_RX.0.Mode=DMA_NORMAL
Dma.SPI1_RX.0.PeriphDataAlignment=DMA_PDATAALIGN_BYTE
Dma.SPI1_RX.0.PeriphInc=DMA_PINC_DISABLE
Dma.SPI1_RX.0.Priority=DMA_PRIORITY_LOW
Dma.SPI1_RX.0.RequestParameters=Instance,Direction,PeriphInc,MemInc,PeriphDataAlignment,MemDataAlignment,Mode,Priority
File.Version=6
GPIO.groupedBy=Show All
KeepUserPlacement=false
Mcu.CPN=STM32F072C8T6TR
Mcu.Family=STM32F0
Mcu.IP0=DMA
Mcu.IP1=NVIC
Mcu.IP2=RCC
Mcu.IP3=SPI1
Mcu.IP4=SYS
Mcu.IP5=TIM14
Mcu.IP6=USB
Mcu.IP7=USB_DEVICE
Mcu.IPNb=8
Mcu.Name=STM32F072C(8-B)Tx
Mcu.Package=LQFP48
Mcu.Pin0=PC13
Mcu.Pin1=PC14-OSC32_IN
Mcu.Pin10=PA11
Mcu.Pin11=PA12
Mcu.Pin12=PA13
Mcu.Pin13=PA14
Mcu.Pin14=PB3
Mcu.Pin15=PB4
Mcu.Pin16=VP_SYS_VS_Systick
Mcu.Pin17=VP_TIM14_VS_ClockSourceINT
Mcu.Pin18=VP_USB_DEVICE_VS_USB_DEVICE_CDC_FS
Mcu.Pin2=PC15-OSC32_OUT
Mcu.Pin3=PF0-OSC_IN
Mcu.Pin4=PA0
Mcu.Pin5=PA1
Mcu.Pin6=PA2
Mcu.Pin7=PA3
Mcu.Pin8=PA4
Mcu.Pin9=PA5
Mcu.PinsNb=19
Mcu.ThirdPartyNb=0
Mcu.UserConstants=
Mcu.UserName=STM32F072C8Tx
MxCube.Version=6.9.1
MxDb.Version=DB.6.0.91
NVIC.DMA1_Channel2_3_IRQn=true\:0\:0\:false\:false\:true\:false\:true\:true
NVIC.ForceEnableDMAVector=true
NVIC.HardFault_IRQn=true\:0\:0\:false\:false\:true\:false\:false\:false
NVIC.NonMaskableInt_IRQn=true\:0\:0\:false\:false\:true\:false\:false\:false
NVIC.PendSV_IRQn=true\:0\:0\:false\:false\:true\:false\:false\:false
NVIC.SPI1_IRQn=true\:0\:0\:false\:false\:true\:true\:true\:true
NVIC.SVC_IRQn=true\:0\:0\:false\:false\:true\:false\:false\:true
NVIC.SysTick_IRQn=true\:3\:0\:false\:false\:true\:false\:true\:false
NVIC.TIM14_IRQn=true\:0\:0\:false\:false\:true\:true\:true\:true
NVIC.USB_IRQn=true\:0\:0\:false\:false\:true\:false\:true\:true
PA0.GPIOParameters=PinState,GPIO_Label
PA0.GPIO_Label=CS0
PA0.Locked=true
PA0.PinState=GPIO_PIN_SET
PA0.Signal=GPIO_Output
PA1.GPIOParameters=PinState,GPIO_Label
PA1.GPIO_Label=CS1
PA1.Locked=true
PA1.PinState=GPIO_PIN_SET
PA1.Signal=GPIO_Output
PA11.Locked=true
PA11.Mode=Device
PA11.Signal=USB_DM
PA12.Mode=Device
PA12.Signal=USB_DP
PA13.Locked=true
PA13.Mode=Serial_Wire
PA13.Signal=SYS_SWDIO
PA14.Mode=Serial_Wire
PA14.Signal=SYS_SWCLK
PA2.GPIOParameters=PinState,GPIO_Label
PA2.GPIO_Label=CS2
PA2.Locked=true
PA2.PinState=GPIO_PIN_SET
PA2.Signal=GPIO_Output
PA3.GPIOParameters=PinState,GPIO_Label
PA3.GPIO_Label=CS3
PA3.Locked=true
PA3.PinState=GPIO_PIN_SET
PA3.Signal=GPIO_Output
PA4.GPIOParameters=GPIO_Label
PA4.GPIO_Label=OUT0
PA4.Locked=true
PA4.Signal=GPIO_Output
PA5.GPIOParameters=GPIO_Label
PA5.GPIO_Label=OUT1
PA5.Locked=true
PA5.Signal=GPIO_Output
PB3.Locked=true
PB3.Mode=RX_Only_Simplex_Unidirect_Master
PB3.Signal=SPI1_SCK
PB4.Locked=true
PB4.Mode=RX_Only_Simplex_Unidirect_Master
PB4.Signal=SPI1_MISO
PC13.GPIOParameters=GPIO_Label
PC13.GPIO_Label=LED3
PC13.Locked=true
PC13.Signal=GPIO_Input
PC14-OSC32_IN.GPIOParameters=GPIO_Label
PC14-OSC32_IN.GPIO_Label=LED2
PC14-OSC32_IN.Locked=true
PC14-OSC32_IN.Signal=GPIO_Input
PC15-OSC32_OUT.GPIOParameters=GPIO_Label
PC15-OSC32_OUT.GPIO_Label=LED1
PC15-OSC32_OUT.Locked=true
PC15-OSC32_OUT.Signal=GPIO_Input
PF0-OSC_IN.GPIOParameters=GPIO_Label
PF0-OSC_IN.GPIO_Label=LED0
PF0-OSC_IN.Locked=true
PF0-OSC_IN.Signal=GPIO_Input
PinOutPanel.RotationAngle=0
ProjectManager.AskForMigrate=true
ProjectManager.BackupPrevious=false
ProjectManager.CompilerOptimize=6
ProjectManager.ComputerToolchain=false
ProjectManager.CoupleFile=true
ProjectManager.CustomerFirmwarePackage=
ProjectManager.DefaultFWLocation=true
ProjectManager.DeletePrevious=true
ProjectManager.DeviceId=STM32F072C8Tx
ProjectManager.FirmwarePackage=STM32Cube FW_F0 V1.11.4
ProjectManager.FreePins=true
ProjectManager.HalAssertFull=false
ProjectManager.HeapSize=0x200
ProjectManager.KeepUserCode=true
ProjectManager.LastFirmware=true
ProjectManager.LibraryCopy=0
ProjectManager.MainLocation=Core/Src
ProjectManager.NoMain=false
ProjectManager.PreviousToolchain=
ProjectManager.ProjectBuild=false
ProjectManager.ProjectFileName=PTC0402K.ioc
ProjectManager.ProjectName=PTC0402K
ProjectManager.ProjectStructure=
ProjectManager.RegisterCallBack=
ProjectManager.StackSize=0x400
ProjectManager.TargetToolchain=Makefile
ProjectManager.ToolChainLocation=
ProjectManager.UAScriptAfterPath=
ProjectManager.UAScriptBeforePath=
ProjectManager.UnderRoot=false
ProjectManager.functionlistsort=1-SystemClock_Config-RCC-false-HAL-false,2-MX_GPIO_Init-GPIO-false-HAL-true,3-MX_DMA_Init-DMA-false-HAL-true,4-MX_SPI1_Init-SPI1-false-HAL-true,5-MX_USB_DEVICE_Init-USB_DEVICE-false-HAL-false,6-MX_TIM14_Init-TIM14-false-HAL-true
RCC.AHBFreq_Value=48000000
RCC.APB1Freq_Value=48000000
RCC.APB1TimFreq_Value=48000000
RCC.CECFreq_Value=32786.88524590164
RCC.FCLKCortexFreq_Value=48000000
RCC.FamilyName=M
RCC.HCLKFreq_Value=48000000
RCC.HSICECFreq_Value=32786.88524590164
RCC.I2SFreq_Value=48000000
RCC.IPParameters=AHBFreq_Value,APB1Freq_Value,APB1TimFreq_Value,CECFreq_Value,FCLKCortexFreq_Value,FamilyName,HCLKFreq_Value,HSICECFreq_Value,I2SFreq_Value,MCOFreq_Value,PLLCLKFreq_Value,PLLMCOFreq_Value,SYSCLKFreq_VALUE,SYSCLKSource,TimSysFreq_Value,USART1Freq_Value,USART2Freq_Value,VCOOutput2Freq_Value
RCC.MCOFreq_Value=48000000
RCC.PLLCLKFreq_Value=16000000
RCC.PLLMCOFreq_Value=16000000
RCC.SYSCLKFreq_VALUE=48000000
RCC.SYSCLKSource=RCC_SYSCLKSOURCE_HSI48
RCC.TimSysFreq_Value=48000000
RCC.USART1Freq_Value=48000000
RCC.USART2Freq_Value=48000000
RCC.VCOOutput2Freq_Value=8000000
SPI1.BaudRatePrescaler=SPI_BAUDRATEPRESCALER_32
SPI1.CalculateBaudRate=1.5 MBits/s
SPI1.DataSize=SPI_DATASIZE_8BIT
SPI1.Direction=SPI_DIRECTION_2LINES_RXONLY
SPI1.IPParameters=VirtualType,Mode,Direction,CalculateBaudRate,DataSize,BaudRatePrescaler,NSSPMode
SPI1.Mode=SPI_MODE_MASTER
SPI1.NSSPMode=SPI_NSS_PULSE_DISABLE
SPI1.VirtualType=VM_MASTER
TIM14.AutoReloadPreload=TIM_AUTORELOAD_PRELOAD_ENABLE
TIM14.IPParameters=Period,AutoReloadPreload
TIM14.Period=48000
USB_DEVICE.CLASS_NAME_FS=CDC
USB_DEVICE.IPParameters=VirtualMode,VirtualModeFS,CLASS_NAME_FS,PRODUCT_STRING_CDC_FS,MANUFACTURER_STRING
USB_DEVICE.MANUFACTURER_STRING=Blueskin Design Ltd
USB_DEVICE.PRODUCT_STRING_CDC_FS=PTC0402K
USB_DEVICE.VirtualMode=Cdc
USB_DEVICE.VirtualModeFS=Cdc_FS
VP_SYS_VS_Systick.Mode=SysTick
VP_SYS_VS_Systick.Signal=SYS_VS_Systick
VP_TIM14_VS_ClockSourceINT.Mode=Enable_Timer
VP_TIM14_VS_ClockSourceINT.Signal=TIM14_VS_ClockSourceINT
VP_USB_DEVICE_VS_USB_DEVICE_CDC_FS.Mode=CDC_FS
VP_USB_DEVICE_VS_USB_DEVICE_CDC_FS.Signal=USB_DEVICE_VS_USB_DEVICE_CDC_FS
board=custom

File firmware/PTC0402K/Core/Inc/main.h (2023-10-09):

/* USER CODE BEGIN Header */
/**
  ******************************************************************************
  * @file           : main.h
  * @brief          : Header for main.c file.
  *                   This file contains the common defines of the application.
  ******************************************************************************
  * @attention
  *
  * Copyright (c) 2023 STMicroelectronics.
  * All rights reserved.
  *
  * This software is licensed under terms that can be found in the LICENSE file
  * in the root directory of this software component.
  * If no LICENSE file comes with this software, it is provided AS-IS.
  *
  ******************************************************************************
  */
/* USER CODE END Header */

/* Define to prevent recursive inclusion -------------------------------------*/
#ifndef __MAIN_H
#define __MAIN_H

#ifdef __cplusplus
extern "C" {
#endif

/* Includes ------------------------------------------------------------------*/
#include "stm32f0xx_hal.h"

/* Private includes ----------------------------------------------------------*/
/* USER CODE BEGIN Includes */

/* USER CODE END Includes */

/* Exported types ------------------------------------------------------------*/
/* USER CODE BEGIN ET */

/* USER CODE END ET */

/* Exported constants --------------------------------------------------------*/
/* USER CODE BEGIN EC */

/* USER CODE END EC */

/* Exported macro ------------------------------------------------------------*/
/* USER CODE BEGIN EM */

/* USER CODE END EM */

/* Exported functions prototypes ---------------------------------------------*/
void Error_Handler(void);

/* USER CODE BEGIN EFP */

/* USER CODE END EFP */

/* Private defines -----------------------------------------------------------*/
#define LED3_Pin GPIO_PIN_13
#define LED3_GPIO_Port GPIOC
#define LED2_Pin GPIO_PIN_14
#define LED2_GPIO_Port GPIOC
#define LED1_Pin GPIO_PIN_15
#define LED1_GPIO_Port GPIOC
#define LED0_Pin GPIO_PIN_0
#define LED0_GPIO_Port GPIOF
#define CS0_Pin GPIO_PIN_0
#define CS0_GPIO_Port GPIOA
#define CS1_Pin GPIO_PIN_1
#define CS1_GPIO_Port GPIOA
#define CS2_Pin GPIO_PIN_2
#define CS2_GPIO_Port GPIOA
#define CS3_Pin GPIO_PIN_3
#define CS3_GPIO_Port GPIOA
#define OUT0_Pin GPIO_PIN_4
#define OUT0_GPIO_Port GPIOA
#define OUT1_Pin GPIO_PIN_5
#define OUT1_GPIO_Port GPIOA

/* USER CODE BEGIN Private defines */

/* USER CODE END Private defines */

#ifdef __cplusplus
}
#endif

#endif /* __MAIN_H */

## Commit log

2023-09-14 Initial commit of Rev 1
    [Assemby.FCStd, Front.FCStd, FrontPanel.kicad_pcb, FrontPanel.kicad_sch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]
2023-09-15 updated title blocks to reflect correct license
    [FrontPanel.kicad_pcb, FrontPanel.kicad_sch, RearPanel.kicad_pcb, TC_Channel.kicad_sch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]
2023-10-09 Update README.md
    Updated project status after receiving boards.
2023-10-25 Added buildtable.c, cleaned up file locations and updated Makefile to automatically build NIST.h
    [Assemby.FCStd, Front.FCStd, PCB.FCStd, PCC-SMP-V-Body.step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]
2023-10-28 added simple bangbang temperature controller and updated test.py to test it

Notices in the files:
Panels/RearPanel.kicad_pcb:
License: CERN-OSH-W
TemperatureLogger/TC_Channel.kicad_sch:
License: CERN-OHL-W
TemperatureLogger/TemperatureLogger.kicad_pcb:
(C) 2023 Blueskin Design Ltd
